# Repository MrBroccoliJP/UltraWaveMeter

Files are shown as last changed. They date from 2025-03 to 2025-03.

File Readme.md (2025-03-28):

 
# UltraWaveMeter 🌊📏

**UltraWaveMeter** is an Arduino-based ultrasonic measurement system designed to measure distances and detect waves using the **HC-SR04** ultrasonic sensor. It is built on the **ESP8266** microcontroller and supports real-time data logging, temperature-compensated calculations, and serial interface control.

<figure>
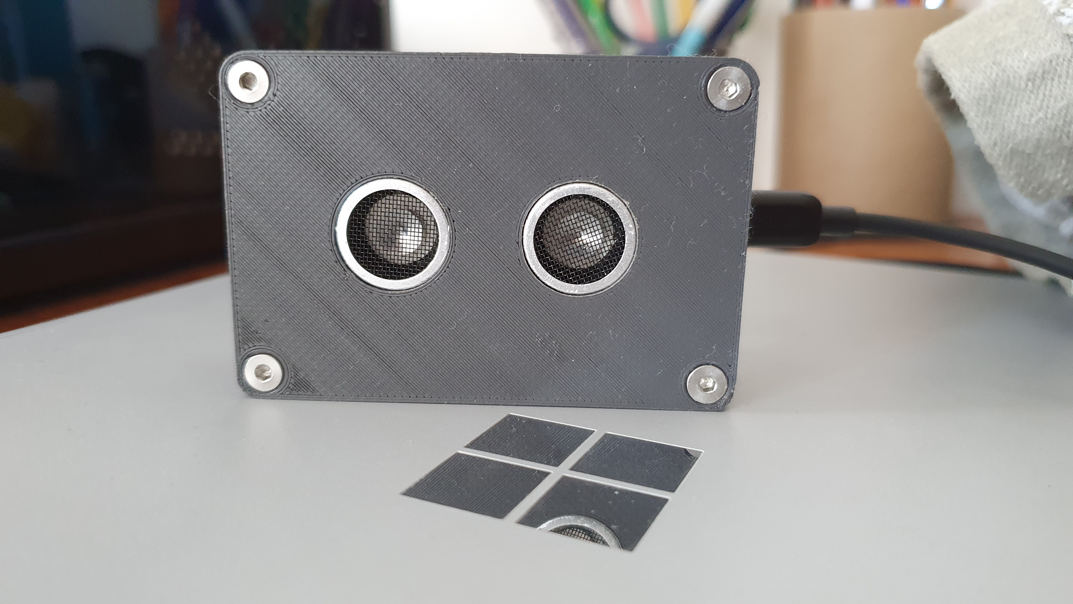
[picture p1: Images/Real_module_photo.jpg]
UltraWaveMeter - Final Assembled Module
    
    <figcaption>UltraWaveMeter - Final Assembled Module</figcaption>
</figure>

## About the Project  

This project was developed in collaboration with the [**Department of Civil Engineering at the University of Aveiro**](https://www.ua.pt/pt/decivil/). It was designed as a measurement device to analyze wave behavior in an artificial canal. The collected wave data was used to study the effects of different materials and techniques for **wave energy dissipation**, specifically in structures like breakwaters and seawalls—such as the **Paredão de Aveiro**.  

The module was custom-built to be attached to the **artificial canal** used for the experiment. Waves were artificially generated using a mechanical system, allowing researchers to test various **frequencies and amplitudes**.  

Upon completion, the module was delivered to a faculty professor along with an **instruction manual**, ensuring that it could be reused and easily adapted for future experiments.  

A prototype featured Wi-Fi connectivity for remote data transmission and control. However, due to time constraints and network configuration complexities, this feature was omitted from the final version.

<figure>
    UltraWaveMeter measuring wave behavior in an artificial canal
    <figcaption>UltraWaveMeter measuring waves in an artificial canal</figcaption>
</figure>

[Video example of the artificial waves](Images/Video.mp4)

## Features
* **Accurate Distance Measurement:** Uses an **HC-SR04** ultrasonic sensor.
* **ESP8266 Microcontroller:** For reliable data processing.
* **Temperature Compensation:** Ensures precise readings.
* **Real-time Serial Monitoring and Logging:** For immediate data analysis.
* **Adjustable Sampling Rate:** Provides flexibility in measurement frequency.
* **Physical Buttons & Remote Trigger:** Offers multiple control options.
* **Serial Commands:** Enables remote operation.
* **Durable Enclosure:** 3D printed using PETG for enhanced durability.

## Components
| Quantity | Component        | Model         |
|----------|-----------------|--------------|
| 1        | Microcontroller  | ESP8266      |
| 1        | Ultrasonic Sensor | HC-SR04     |
| 1        | Red LED         | Generic      |
| 1        | Resistor (330Ω) | Generic      |
| 3        | Push Button     | Generic      |
| 1        | USB Cable (Micro-USB)* | Generic |

###### *depends on the dev board used
## Wiring Diagram
The setup connects the **HC-SR04** sensor to the **ESP8266**, along with buttons for user input and an LED indicator. Ensure correct wiring to prevent malfunctions.   
BTN2 is a remote trigger button connected via a JST plug.

**Pin Assignments:**

| Component         | Pin  | GPIO |
|-------------------|------|------|
| BTN1              | D3   | GPIO 0|
| BTN2              | SD3  | GPIO 10|
| LED               | D0   | GPIO 16|
| RST Button        | RST  |    |
| HC-SR04 Trigger   | D6   | GPIO 13|
| HC-SR04 Echo      | D7   | GPIO 15|

<figure>
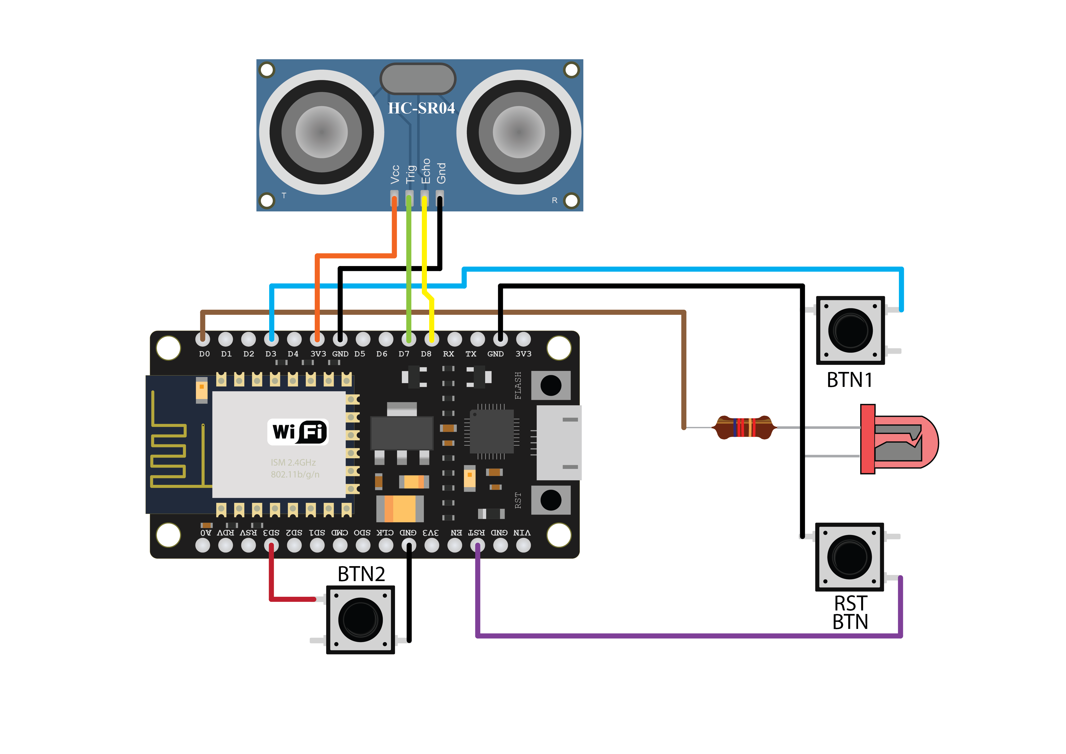
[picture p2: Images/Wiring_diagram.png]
UltraWaveMeter wiring diagram
    
    <figcaption>UltraWaveMeter wiring diagram </figcaption>
</figure>

<figure>
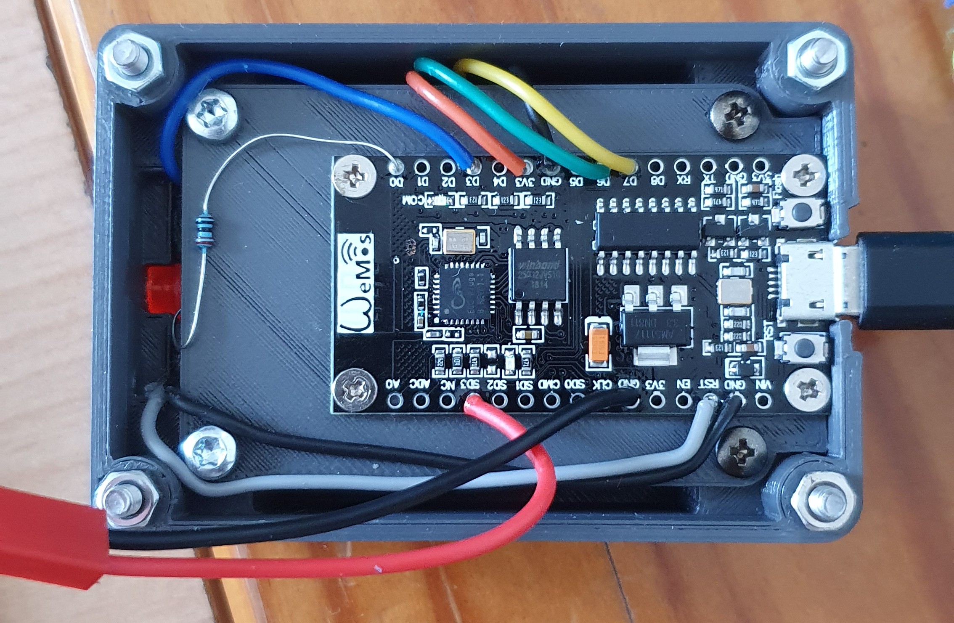
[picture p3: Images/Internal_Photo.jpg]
UltraWaveMeter internal photo
    
    <figcaption>UltraWaveMeter internal wiring and assembly </figcaption>
</figure>

## 3D Model and assembly 

The 3D model consists of three main parts. The shell is made up of two sections that screw together, forming a water-resistant enclosure for the electrical components. The ultrasonic sensor is securely held in place at the bottom, fitting snugly within the housing and pressed together with a tray that houses the ESP8266 dev board. The design prioritizes ease of assembly and maintenance, allowing for quick repairs in case of failure.

<figure>
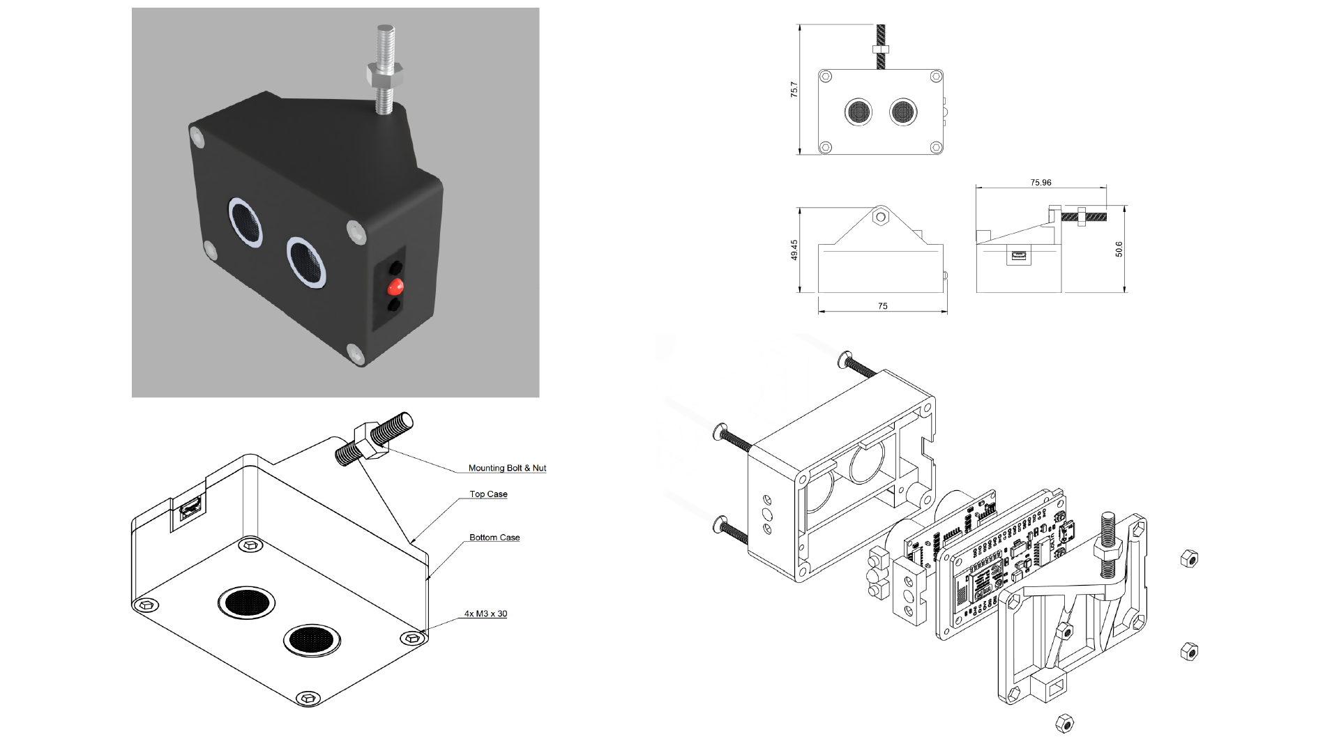
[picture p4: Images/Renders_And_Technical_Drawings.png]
3D Model, Renders, and Technical Drawings of the UltraWaveMeter Enclosure
    
    <figcaption>3D Model, Renders, and Technical Drawings of the UltraWaveMeter Enclosure </figcaption>
</figure>

The top and bottom enclosures are screwed together with an insulating material (silicone glue or a rubber gasket) to prevent water ingress, with additional silicone glue applied around the ultrasonic module tubes for further sealing.

### Remote Trigger Button (BTN2)

 - BTN2 uses a JST connector, glued and insulated to prevent water ingression, and a 3-meter cable for remote operation.  
  
<figure>
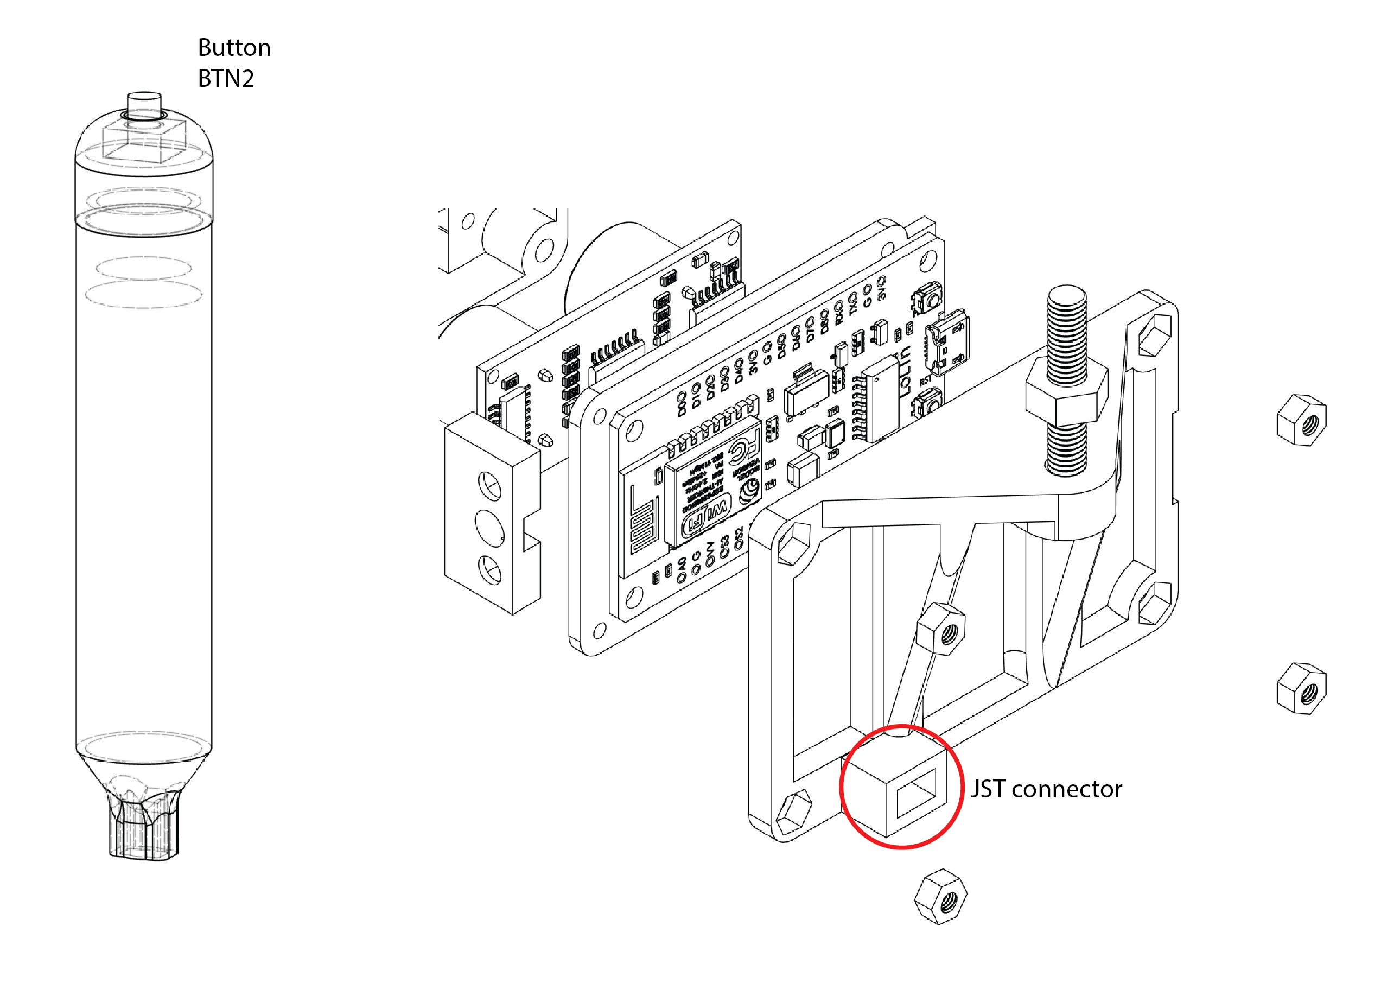
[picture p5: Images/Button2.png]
Waterproof Remote Trigger Button (BTN2) with JST Connector
    
    <figcaption>Waterproof Remote Trigger Button (BTN2) with JST Connector </figcaption>
</figure>

## Usage Instructions
1.  **Position:** Place the module above the measurement area.
2.  **Connect:** Connect the USB cable to a computer.
3.  **Open Serial Monitor:** Set the baud rate to 9600.
4.  **Temperature Input:** Enter the ambient temperature when prompted.
5.  **Start Measurement:**
    * Press Button 1, Button 2, or enter 'S' in the serial monitor.
    * Default sampling interval is 40ms.
    * To change, enter 'N' and specify a value >40ms.
6.  **Stop Measurement:**
    * Press Button 1, Button 2, or enter 'S'.
7.  **Save Data:**
    * Copy the serial monitor output for analysis.
8.  **Reset:**
    * Enter 'R' or press the reset button.

## Arduino Code / Sketch

### Deprecated Code
The version of the code in **Original_Portuguese** is now deprecated and is no longer actively maintained. Please use the version in **Translated_English** for the most up-to-date version of the software.

- **[Original Version (Portuguese)](Arduino_Sketch/Original_Portuguese/UltraWaveMeter/UltraWaveMeter.ino)** - Deprecated
- **[Updated Version (English)](Arduino_Sketch/Translated_English/UltraWaveMeter/UltraWaveMeter.ino)** - Recommended

## How the Sensor Works
The **HC-SR04** ultrasonic sensor emits a **40 kHz** sound wave that reflects off objects. The sensor calculates the time taken for the wave to return and determines the distance using the formula:

$$
\text{Distance (cm)} = \frac{\text{Speed of Sound (cm/μs)} \times \text{Echo Signal Duration (μs)}}{2}
$$  

With temperature compensation:  

$$
\text{Distance} = 0.034 \times \frac{\text{Echo}}{2} \times \frac{1 + T}{273.15} \times 60.368
$$  

## Example Output
<details>
  <summary>Example</summary>

```
PROGRAM STARTING

Enter ambient temperature: 23
23
Temperature saved
===== Program Initialized =====

Baseline distance: 124,5 cm 
Baseline distance: 125,1 cm 

Average: 124,8 cm 

Version: V5.0

Ultrasonic Wave Measurement System
To start measurements, press Button 1, Button 2, or enter 'S' in serial console.
To stop, press Button 1, Button 2, or enter 'S' in serial console.
To use a custom sample interval (default = 40ms), enter 'N'.
To RESET the system, enter 'R'.
****************************

Waiting to start -> Press Button 1 or Button 2 or enter 'S' OR 'N'
S

********** READING NUMBER: 1 **********
Baseline distance: 124,8 cm 
Baseline distance: 125,2 cm 
Baseline distance: 124,9 cm 
Baseline distance: 125,0 cm 
Baseline distance: 125,3 cm 

Baseline distance: Average = 125,04 cm 

Sample interval: 40ms 

DISTANCE (cm) || TIME (ms)

125,04 40
125,05 80
125,12 120
125,08 160
125,11 200
124,98 240
120,34 280
115,22 320
110,15 360
105,47 400
100,32 440
95,78 480
90,23 520
85,69 560
90,14 600
95,33 640
100,21 680
105,67 720
110,45 760
115,22 800
120,11 840
124,76 880
124,88 920
124,93 960
125,02 1000
S

Waiting to start -> Press Button 1 or Button 2 or enter 'S' OR 'N'
N

MODE 2

Enter desired sample interval in ms (minimum 40ms): 100
(...)
```

</details>

The data was then copied into Excel, where graphs were generated, and average, minimum, and maximum measurements were calculated. Relevant equations were applied to analyze the wave behavior and energy dissipation.

<figure>
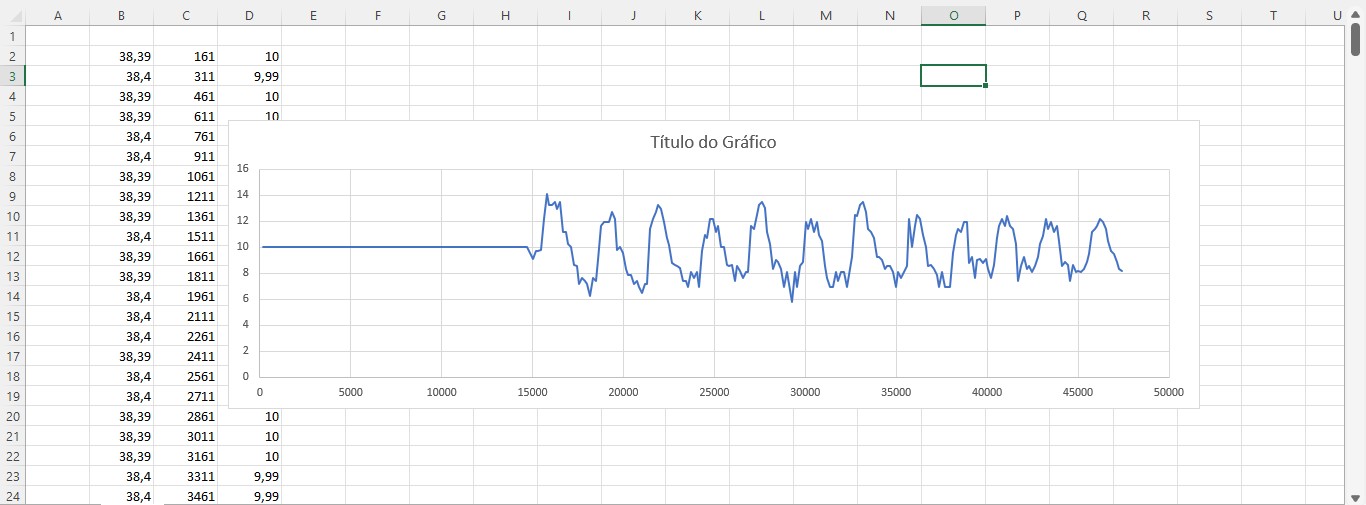
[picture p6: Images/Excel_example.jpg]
Analyzing UltraWaveMeter Data in Excel - Wave Behavior Graphs
    
    <figcaption>Analyzing UltraWaveMeter Data in Excel - Wave Behavior Graphs </figcaption>
</figure>

## Software
The system is programmed using **Arduino IDE** with the **NewPing** library by Tim Eckel. The library simplifies sensor interactions and improves accuracy.

### Useful Links
- [Arduino NewPing Library](https://www.arduino.cc/reference/en/libraries/newping/)
- [NewPing Documentation](https://bitbucket.org/teckel12/arduino-new-ping/wiki/Home)

------
## 📜 License
Developed by **João Fernandes**  

This project is licensed under the Creative Commons Attribution-NonCommercial 4.0 International License (CC BY-NC 4.0)

UltraWaveMeter © 2022-2025 by João Fernandes is licensed under Creative Commons Attribution-NonCommercial 4.0 International  

See the [LICENSE](LICENSE.txt) file for details  
Or visit:  
[http://creativecommons.org/licenses/by-nc/4.0/](http://creativecommons.org/licenses/by-nc/4.0/)  

or send a letter to:

Creative Commons
PO Box 1866  
Mountain View,    
CA 94042  
USA  

In summary (not a substitute for the full license):

 - You are free to share and adapt the material for non-commercial purposes
 - You must give appropriate credit and indicate if changes were made
 - You may not use the material for commercial purposes without specific permission

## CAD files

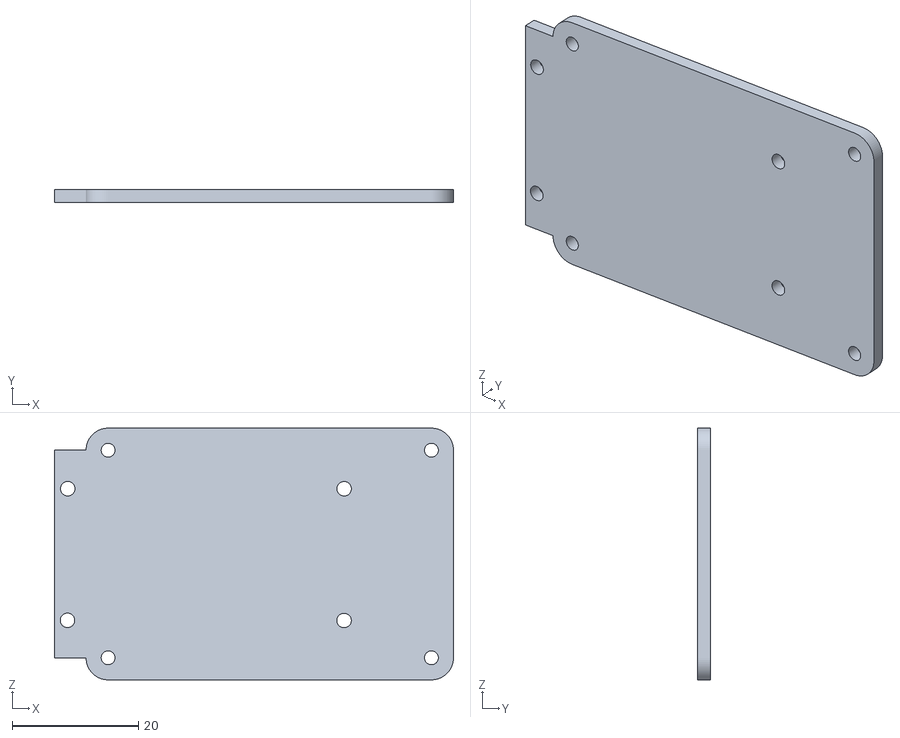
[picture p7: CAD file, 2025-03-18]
3D_Models/STL/Inner_esp_mounting_tray.stl
63.3 x 2.00 x 39.9

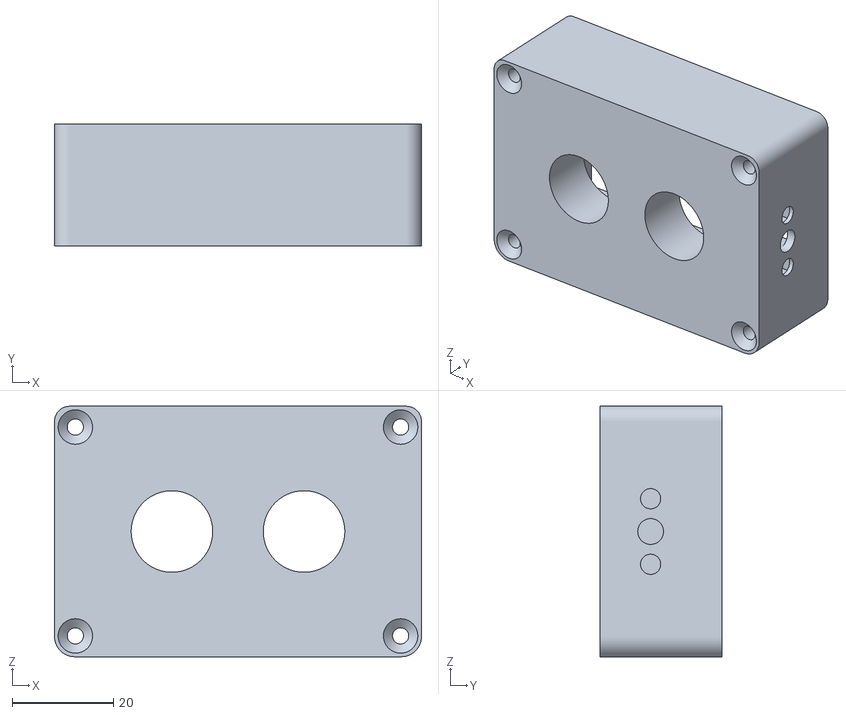
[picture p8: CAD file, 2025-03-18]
3D_Models/STL/Bot_case.stl
72.5 x 24.1 x 49.5

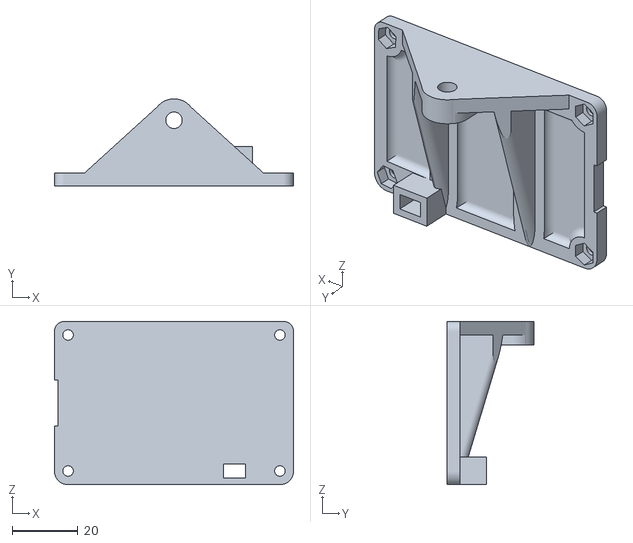
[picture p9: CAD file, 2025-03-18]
3D_Models/STL/Top_case.stl
72.5 x 26.5 x 49.5

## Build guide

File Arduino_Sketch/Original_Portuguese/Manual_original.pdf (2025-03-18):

# Sensor ultrassónico para medição de ondas

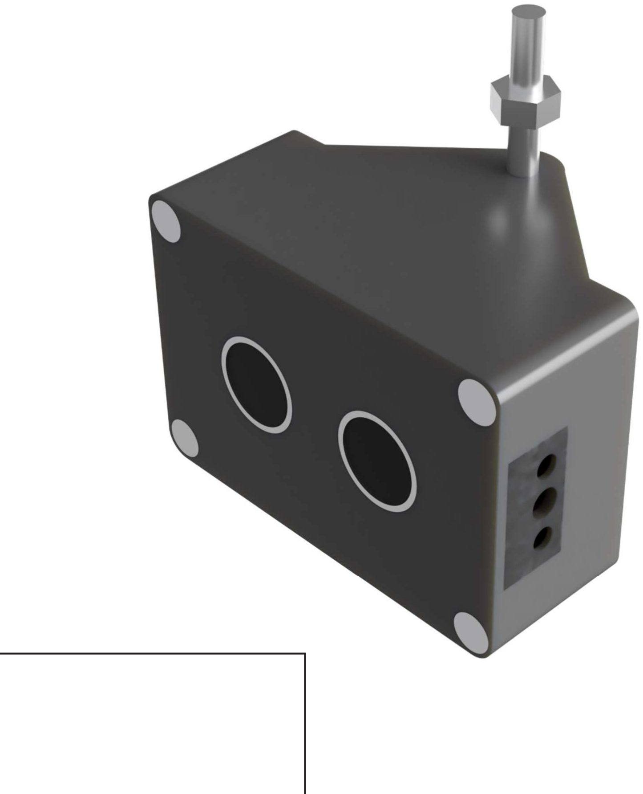
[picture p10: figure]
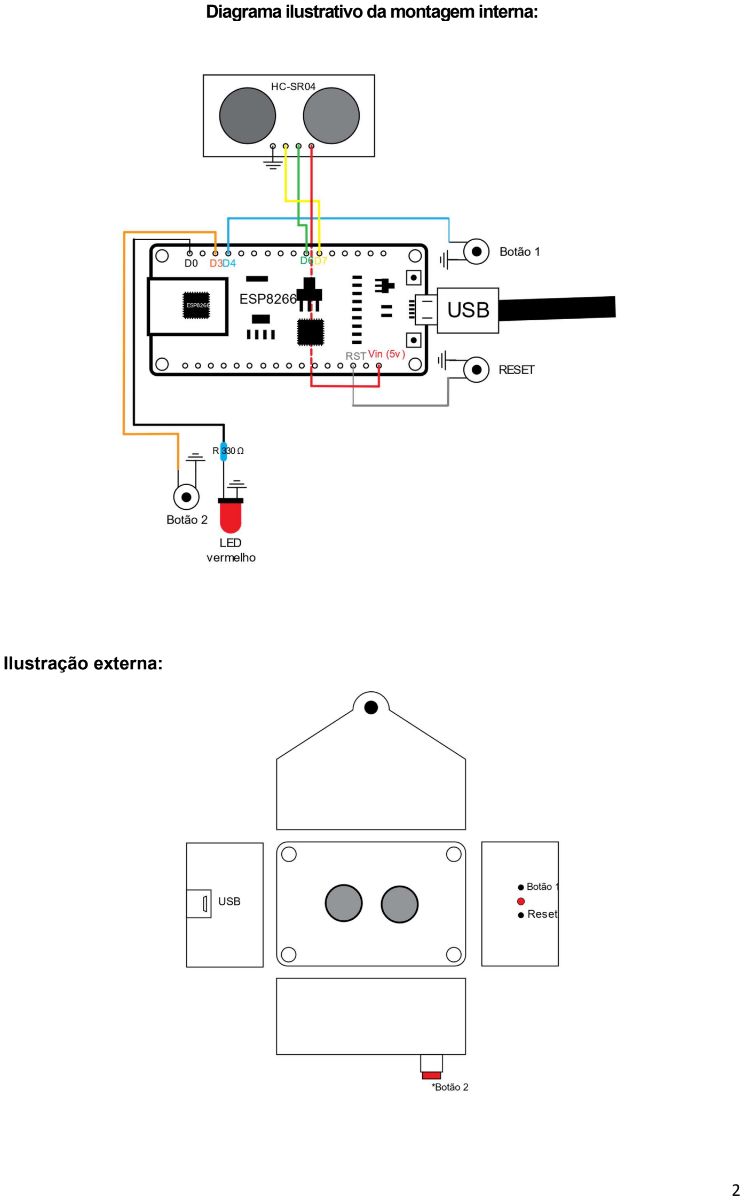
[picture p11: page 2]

Diagrama ilustrativo da montagem interna:

Ilustração externa:

Tabela de componentes:

QUANTIDADE | TIPO | MODELO
1 | Microcontrolador | ESP8266
1 | Sensor ultrassónico | HC-SR04
1 | LED vermelho | Genérico
1 | Resistência (330 Ω) | Genérico
3 | Botão momentâneo | Genérico

### 1 Cabo Micro-USB para USB

| 3m | Genérico

Instruções de uso:
1. Colocar o módulo numa posição acima do sítio onde se pretende efetuar a medida.
2. Ligar o cabo USB a um computador.

### 3. Abrir um programa com capacidade de monitor de série (por ex. Arduíno IDE):

a. Selecionar a taxa de transmissão recebida a: 9600

### 4. Seguir as instruções que serão mostradas no ecrã:

a. Inserir a temperatura ambiente e enviar

### 5. Começar uma contagem:

a. Usando o Botão 1, Botão 2 ou enviando “S” pelo monitor de série começa uma contagem com 40ms de intervalo entre cada medição.
b. Enviando “N” pelo monitor de série é possível começar uma nova medição com o intervalo entre amostras parametrizável:
i. Envie pelo monitor de série o intervalo que pretende (>40ms)

### 6. Parar uma contagem: Usando o Botão 1, Botão 2 ou enviando “S” pelo monitor de

série.

### 7. Copiar os dados do monitor de série e guardar num ficheiro a escolha, para

tratamento dos mesmos posteriormente.

Observação:

### 1. Se for necessário fazer reset ao microcontrolador pode-se enviar “R” pelo monitor de

série ou clicando no botão reset.

### 2. Para uso com Arduino ide: Arduino IDE -> Ferramentas -> Monitor

Observações finais:

O módulo é composto por um sensor ultrassónico “HC-SR04” que mede a distância de qualquer objeto até ao mesmo. Tem uma resolução de 0.3 Cm o que faz com que cada medida tenha uma incerteza de ±0.3Cm, tem alcance de 2cm até 400cm.

O sensor é composto por um transmissor e recetor, transmite uma onda com frequência de 40 kHz. Quando transmite a onda a onda é refletida e a mesma demora mais ou menos tempo dependendo da distância a que está o objeto. O sensor contém 4 conexões, sendo duas das mesmas de energia, e as duas de comunicação, um desses portos é denominada por “trigger” e outro é denominado de “echo”. Para ser efetuada uma medida o porto “trigger” tem de ser enviado um sinal alto durante 10µs, o módulo é então assim sinalizado que se pretende fazer uma medição. De seguida envia 8 sinais de 40kHz, através do envio de 8 sinais consegue minimizar o erro devido a interferências externas. Se nenhum dos sinais for obtido no transmissor o sensor envia um sinal alto através do porto “Echo” durante 38ms que sinaliza que a leitura não foi efetuada corretamente (Time-out). Se o sensor receber os sinais transmitidos coloca o porto “Echo” em sinal alto durante o tempo que o sinal demorou desde que foi transmitido até ser recebido. Usando esse tempo, podemos calcular a distância de um objeto relativamente ao sensor através da velocidade do som.

# ܦݐݏ ݋݋݋ ݏߤ

# ݏߤEcho݋݋ ݎݑܦ

# ܦݐݏ

Echo

Visto que a velocidade do som está relacionada com a densidade do material de propagação, e a densidade está por sua vez relacionada com a temperatura a que se encontra esse material, a equação teve de ser ajustada tendo em conta a temperatura ambiente.

# ܦݐݏ

Echo

כ

*Fórmula utilizada por recomendação dos criadores da livraria “NewPing”
Para operar o sensor foi usado um microcontrolador, neste caso baseado no microchip ESP8266. A tarefa deste microcontrolador coordenar os pedidos de leitura ao sensor e de seguida processar os dados que o sensor transmite para a distância em centímetros usando a fórmula acima.

O microcontrolador foi programado usando programação arduino. No código foi usada uma livraria “NewPing”, escrita por “Tim Eckel“, esta livraria foi escrita para agilizar o uso deste tipo de sensores sendo esta uma forma mais fácil e intuitiva de interagir com o sensor através do micro controlador. A livraria agilizou o desenvolvimento da interface e a mitigação de erros de medida pelo processamento de dados.

Links uteis:
https://www.arduino.cc/reference/en/libraries/newping/

Documentação:
https://bitbucket.org/teckel12/arduino-new-ping/wiki/Home

Em anexo está o código que foi escrito no microcontrolador à data.
Corresponde á Versão 5 do programa “Sensor ultrassónico para medição de ondas” programado em Arduíno.

João Fernandes

### 29 de Julho de 2022

1 //JOAO FERNANDES 2022
2 //SENSOR ULTRASONICO P
3
4
5 #include <NewPing.h>
6 #define TRIGGER_PIN 12 // Arduino pin tied to trigger pin on the ultrasonic sensor.
7 | #define ECHO_PIN 13 // Arduino pin tied to echo pin on the ultrasonic sensor.
8 #define MAX_DISTANCE 170 // Maximum distance we want to ping for (in centimeters). 9
10 NewPing sonar(TRIGGER_PIN, ECHO_PIN, MAX_DISTANCE); // NewPing setup of pins and maximum distance.
11
12 float temp = 25; // Temperature in Celsius (this value would probably come from a temperature sensor).
13 float factor = sqrt(1 + temp / 273.15)/ 60.368; // Speed of sound calculation based on temperature. //default value 25º
14 short int Mode = 0;
15 bool btnState;
16 unsigned long lastButtonPress = 0;
17 short int btnDelay = 250; //delay for debouncing 18 short int readingN = 0;
19 unsigned long ReadingStart = 0;
20 String READING;
21 String mydata;
22 float avg = 0;
23 String inst = "\nJoão Fernandes 2022\n Para começar leituras clique no botão 1, botão 2 ou insira 'S' no comando de série.\n Para parar clique no botão 1, botão 2 ou insira 'S' no comando de série.\n Para fazer uma leitura com um numero diferente de tempo entre amostras (default = 40ms) envie 'N'\n Para RESET envie 'R'";
24 String Code_version = "V5.0";
25 short int Rate = 40; //default
26
27 void setup() {
28 Serial.begin(9600);
29 pinMode(16, OUTPUT);
30 pinMode(0, INPUT_PULLUP); 31 pinMode(4, INPUT_PULLUP); 32
33 digitalWrite(16, HIGH); 34 delay(100);
35 digitalWrite(16, LOW);
36 delay(500);
37 digitalWrite(16, HIGH); 38 delay(100);
39 digitalWrite(16, LOW);
40 delay(1000);
41 Serial.print("\nPROGRAMA A INICIAR \n");
42 Serial.print("\nInsira a temperatura ambiente: "); 43
44 // while(!Serial.available()) {
45 while (!Serial || !Serial.available()) {
46
47 if (millis() % 250 == 0){
48 digitalWrite(16, HIGH);
49 }
50 else if (millis() % 100 == 0){ 51 digitalWrite(16, LOW);
52 }
53 if (millis() % 3000 == 0){
54 Serial.print("\nInsira a temperatura ambiente: "); 55 Serial.flush();
56 }
57 yield();
58 }
59
60
61 while (mydata.toInt() == 0){
62 mydata = Serial.readStringUntil('\n');
63 Serial.println(mydata);
64 Serial.println("Temperatura guardada\n===== Programa Iniciado =====\n"); 65 Serial.flush();
66 yield();
67 }

### 68 temp = mydata.toInt(); // Temperature in Celsius (this value would probably come

from a temperature sensor).

### 69 factor = sqrt(1 + temp / 273.15)/ 60.368; // Speed of sound calculation based on

temperature. //default value 25º 70
71 for (int i = 2; i > 0; i--) {
72 float readingB = ((float)sonar.ping_median(5)* factor); 73 avg = avg + readingB;
74 READING = "Distancia BASE: " +(String)readingB + " cm "; 75 READING.replace(".", ",");
76 Serial.println(READING);
77 delay(300);
78 }
79 avg = avg / 2;
80 READING = "\nMedia: " +(String)avg + " cm "; 81 READING.replace(".", ",");
82 Serial.println(READING);
83 Serial.print("\n Versão: ");
84 Serial.println(Code_version);
85 Serial.println(inst);
86 Serial.println("****************************\n");
87
88 Serial.println("A aguardar inicio -> Botão 1 ou Botão 2 ou escreva 'S' OU 'N' "); 89 Mode = 0;
90 }
91
92 void loop() {
93
94
95 if (Mode == 0){
96 mydata = "";
97 while (Mode == 0){
98
99
100 if (millis() % 500 == 0){ 101 digitalWrite(16, HIGH); 102 }
103 else if (millis() % 250 == 0){ 104 digitalWrite(16, LOW);
105 }
106
107 if (Serial.available() > 0){
108 mydata = Serial.readStringUntil('\n'); 109 Serial.println(mydata);
110
111 if (mydata == "S"){
112 Mode = 1;
113 Serial.flush();
114 }
115 else if (mydata == "R"){ 116 ESP.reset();
117 }
118 else if (mydata == "N"){ 119 Mode = 2;
120 Serial.flush();
121 }
122 else {
123 Serial.println("Modo inválido -> 'S' OU 'N'"); 124 mydata = "";
125 Serial.flush();
126 }
127 }
128
129 btnState = digitalRead(0); // read input value 130 if (btnState == LOW){
131 if (millis() - lastButtonPress > btnDelay){ 132 Mode = 1;
133 btnState == HIGH;
134 }
135 lastButtonPress = millis();
136 }
137 btnState = digitalRead(4); // read input value 138 if (btnState == LOW){

139 if (millis() - lastButtonPress > btnDelay){ 140 Mode = 1;
141 btnState == HIGH;
142 }
143 lastButtonPress = millis(); 144 }
145 yield();
146 }
147 }
148
149 else if (Mode == 2){
150 Rate = 0;
151 avg = 0;
152
153 Serial.print("\nMODO 2\n" );
154 Serial.print("\nInsira o numero de ms entre amostras pretendido (minimo 40ms): " );
155
156 while (Rate < 40){
157 if (Serial.available() > 0){
158 mydata = Serial.readStringUntil('\n');
159 if (mydata.toInt() > 40 && mydata.toInt() < 5000){ 160 Rate = mydata.toInt();
161 Serial.flush();
162 }
163 else if (mydata == "R"){ 164 ESP.reset();
165 }
166 else if (mydata == "S"){ 167 Mode = 0;
168 Serial.flush();
169 break;
170 }
171 else {
172 Serial.println("\nValor Inválido ('R' PARA RESET & 'S' Para voltar ao menu inicial)\nInsira um valor >40ms" ); 173 Serial.flush();
174 }
175 | // Serial.println(mydata);
176 | // Serial.println(mydata.toInt());
177 }
178 yield();
179 }
180
181 readingN++;
182 if(Mode != 0){
183 Serial.print("\n********** LEITURA NUMERO: " ); 184 Serial.print(readingN );
185 Serial.println(" **********" );
186
187 for (int i = 5; i > 0; i--) {
188 float readingB = ((float)sonar.ping_median(5)* factor); 189 avg = avg + readingB;
190 READING = "Distancia BASE: " +(String)readingB + " cm "; 191 READING.replace(".", ",");
192 Serial.println(READING);
193 delay(300);
194 }
195 avg = avg / 5;
196 READING = "\nDistancia BASE: Média = " +(String)avg + " cm "; 197 READING.replace(".", ",");
198 Serial.println(READING);
199 Serial.print("\nDISTÂNCIA (cm) || TEMPO (ms)\n\n");
200
201 ReadingStart = millis();
202 }
203
204 while (Mode != 0){
205
206 digitalWrite(16, HIGH);
207
208 if (Serial.available() > 0){
209 mydata = Serial.readStringUntil('\n');

210 if (mydata == "S"){
211 Mode = 0;
212 Serial.flush();
213 }
214 if (mydata == "R"){
215 ESP.reset();
216 }
217 }
218
219
220 btnState = digitalRead(0); // read input value 221 if (btnState == LOW){
222 if (millis() - lastButtonPress > btnDelay){ 223 Mode = 0;
224 btnState == HIGH;
225 }
226 lastButtonPress = millis();
227 }
228 btnState = digitalRead(4); // read input value 229 if (btnState == LOW){
230 if (millis() - lastButtonPress > btnDelay){ 231 Mode = 0;
232 btnState == HIGH;
233 }
234 lastButtonPress = millis(); 235 }
236
237 if (millis() % Rate == 0){
238
239 READING = String(((float)sonar.ping_median(1)* factor), 2)+ " " +(String)( millis() - ReadingStart)+ "\n" ; 240 READING.replace(".", ",");
241 Serial.print(READING);
242 Serial.flush();
243 }
244
245 yield();
246 }
247 }
248
249 else {
250 avg = 0;
251 readingN++;
252 Serial.print("\n********** LEITURA NUMERO: " ); 253 Serial.print(readingN );
254 Serial.println(" **********" );
255 | // Serial.print("BASE: ");
256 | // Serial.print(avg);
257 for (int i = 5; i > 0; i--) {
258 float readingB = ((float)sonar.ping_median(5)* factor); 259 avg = avg + readingB;
260 READING = "Distancia BASE: " +(String)readingB + " cm "; 261 READING.replace(".", ",");
262 Serial.println(READING);
263 delay(300);
264 }
265 avg = avg / 5;
266 READING = "\nDistancia BASE: Média = " +(String)avg + " cm ";
267 READING.replace(".", ",");
268 Serial.println(READING);
269 Serial.print("\n Intervalo de tempo entre amostras: 40ms \n\n DISTÂNCIA (cm) || TEMPO (ms)\n\n");
270
271 ReadingStart = millis();
272
273 while (Mode != 0){
274
275
276 digitalWrite(16, HIGH);
277
278 if (Serial.available() > 0){
279 mydata = Serial.readStringUntil('\n'); 280

281 if (mydata == "S"){
282 Mode = 0;
283 Serial.flush();
284 }
285 else if (mydata == "R"){ 286 ESP.reset();
287 }
288 else {
289 Serial.flush();
290 }
291 }
292
293
294 btnState = digitalRead(0); // read input value 295 if (btnState == LOW){
296 if (millis() - lastButtonPress > btnDelay){ 297 Mode = 0;
298 btnState == HIGH;
299 }
300 lastButtonPress = millis();
301 }
302 btnState = digitalRead(4); // read input value 303 if (btnState == LOW){
304 if (millis() - lastButtonPress > btnDelay){ 305 Mode = 0;
306 btnState == HIGH;
307 }
308 lastButtonPress = millis(); 309 }
310
311 if (millis() % 40 == 0){
312
313 READING = String(((float)sonar.ping_median(1)* factor), 2)+ " " +(String)( millis() - ReadingStart)+ "\n" ; 314 READING.replace(".", ",");
315 Serial.print(READING);
316 Serial.flush();
317 }
318
319 yield();
320 }
321 }
322
323 }
324
325 | //JOAO FERNANDES 2022 | -
326

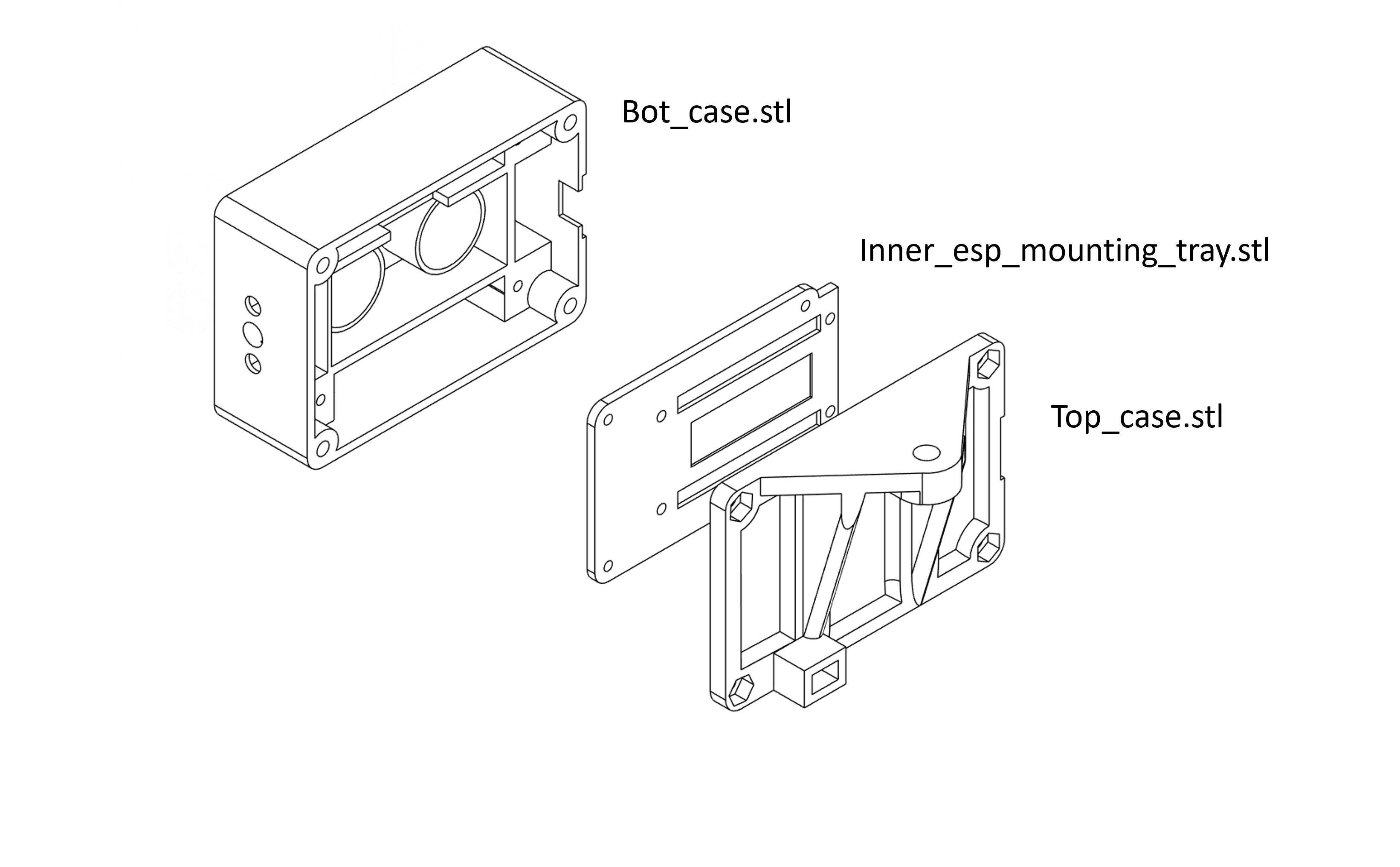
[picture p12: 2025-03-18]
3D_Models/3D_print_files_UltraWaveMeter.png

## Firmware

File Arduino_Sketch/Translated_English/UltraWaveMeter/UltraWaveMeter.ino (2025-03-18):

/**
 * UltraWaveMeter - Ultrasonic measurement system designed for precise distance and wave detection
 * Copyright (c) 2022-2025 João Fernandes
 * 
 * This work is licensed under the Creative Commons Attribution-NonCommercial 
 * 4.0 International License. To view a copy of this license, visit:
 * http://creativecommons.org/licenses/by-nc/4.0/
 * 
 * @author João Fernandes (Original author)
 * @version 6.0
 * @date 2022 (Original)
 * @date 2025 (Translation)
 * 
 * This program uses an ultrasonic sensor to measure distances over time,
 * which can be used for wave measurement applications. It provides different
 * measurement modes and outputs data via serial communication.
 */

#include <NewPing.h>

// Hardware configuration
#define TRIGGER_PIN 13     // Arduino pin connected to the ultrasonic sensor's trigger pin
#define ECHO_PIN 15        // Arduino pin connected to the ultrasonic sensor's echo pin
#define MAX_DISTANCE 170   // Maximum measurable distance in centimeters
#define LED_PIN 16         // Status LED pin
#define BUTTON_1_PIN 0     // First control button (INPUT_PULLUP) BTN1
#define BUTTON_2_PIN 10     // Second control button (INPUT_PULLUP) BTN2

// Initialize ultrasonic sensor with NewPing library
NewPing sonar(TRIGGER_PIN, ECHO_PIN, MAX_DISTANCE);

// Environment and calibration variables
float temp = 25;                        // Default ambient temperature in Celsius
float soundSpeedFactor;                 // Factor to calculate speed of sound based on temperature
float baselineAverage = 0;              // Average baseline measurement

// Program control variables
short int currentMode = 0;              // Operating mode (0: standby, 1: standard measurement, 2: custom interval)
bool buttonState;                       // Current state of buttons
unsigned long lastButtonPress = 0;      // Timestamp of last button press for debouncing
short int buttonDebounceDelay = 250;    // Delay for button debounce in milliseconds
short int readingCount = 0;             // Counter for measurement sessions
unsigned long measurementStartTime = 0; // Timestamp when measurement session started
short int sampleInterval = 40;          // Default time between samples in milliseconds (minimum 40ms)

// Serial communication variables
String measurementData;                 // Holds formatted measurement data for output
String serialInput;                     // Holds input from serial port

// User instructions and program information
String instructions = "\nUltrasonic Wave Measurement System\n"
                      "To start measurements, press Button 1, Button 2, or enter 'S' in serial console.\n"
                      "To stop, press Button 1, Button 2, or enter 'S' in serial console.\n"
                      "To use a custom sample interval (default = 40ms), enter 'N'.\n"
                      "To RESET the system, enter 'R'.";
String codeVersion = "V6.0";

/**
 * Initial setup function - runs once at program start
 */
void setup() {
  // Initialize serial communication
  Serial.begin(9600);
  
  // Configure pin modes
  pinMode(LED_PIN, OUTPUT);
  pinMode(BUTTON_1_PIN, INPUT_PULLUP);
  pinMode(BUTTON_2_PIN, INPUT_PULLUP);

  // LED startup sequence for visual confirmation
  digitalWrite(LED_PIN, HIGH);
  delay(100);
  digitalWrite(LED_PIN, LOW);
  delay(500);
  digitalWrite(LED_PIN, HIGH);
  delay(100);
  digitalWrite(LED_PIN, LOW);
  delay(1000);
  
  // Print startup message
  Serial.print("\nPROGRAM STARTING\n");
  Serial.print("\nEnter ambient temperature: ");

  // Wait for temperature input while blinking the LED
  while (!Serial || !Serial.available()) {
    // Blink LED while waiting
    if (millis() % 250 == 0) {
      digitalWrite(LED_PIN, HIGH);
    }
    else if (millis() % 100 == 0) {
      digitalWrite(LED_PIN, LOW);
    }
    
    // Periodically repeat the prompt
    if (millis() % 3000 == 0) {
      Serial.print("\nEnter ambient temperature: ");
      Serial.flush();
    }
    yield();  // Allow ESP8266 to handle system tasks
  }

  // Process temperature input
  serialInput = "";
  while (serialInput.toInt() == 0) {
    serialInput = Serial.readStringUntil('\n');
    Serial.println(serialInput);
    Serial.println("Temperature saved\n===== Program Initialized =====\n");
    Serial.flush();
    yield();
  }
  
  // Set temperature and calculate sound speed factor
  temp = serialInput.toInt();
  soundSpeedFactor = sqrt(1 + temp / 273.15) / 60.368;  // Speed of sound calculation based on temperature

  // Take initial baseline measurements
  for (int i = 2; i > 0; i--) {
    float baselineReading = ((float)sonar.ping_median(5) * soundSpeedFactor);
    baselineAverage += baselineReading;
    measurementData = "Baseline distance: " + (String)baselineReading + " cm ";
    measurementData.replace(".", ",");  // Format for CSV compatibility
    Serial.println(measurementData);
    delay(300);
  }
  
  // Calculate and display average baseline
  baselineAverage = baselineAverage / 2;
  measurementData = "\nAverage: " + (String)baselineAverage + " cm ";
  measurementData.replace(".", ",");
  Serial.println(measurementData);
  
  // Output program information and instructions
  Serial.print("\nVersion: ");
  Serial.println(codeVersion);
  Serial.println(instructions);
  Serial.println("****************************\n");
  Serial.println("Waiting to start -> Press Button 1 or Button 2 or enter 'S' OR 'N'");
  
  // Set initial mode to standby
  currentMode = 0;
}

/**
 * Main program loop
 */
void loop() {
  // MODE 0: Standby - waiting for user input to start measurement
  if (currentMode == 0) {
    serialInput = "";
    while (currentMode == 0) {
      // Status LED blink pattern for standby mode
      if (millis() % 500 == 0) {
        digitalWrite(LED_PIN, HIGH);
      }
      else if (millis() % 250 == 0) {
        digitalWrite(LED_PIN, LOW);
      }

      // Check for serial commands
      if (Serial.available() > 0) {
        serialInput = Serial.readStringUntil('\n');
        Serial.println(serialInput);

        // Process commands
        if (serialInput == "S") {
          currentMode = 1;  // Start standard measurement
          Serial.flush();
        }
        else if (serialInput == "R") {
          ESP.reset();      // Reset the system
        }
        else if (serialInput == "N") {
          currentMode = 2;  // Start custom interval measurement
          Serial.flush();
        }
        else {
          Serial.println("Invalid mode -> Use 'S' OR 'N'");
          serialInput = "";
          Serial.flush();
        }
      }

      // Check Button 1 state
      buttonState = digitalRead(BUTTON_1_PIN);
      if (buttonState == LOW) {
        if (millis() - lastButtonPress > buttonDebounceDelay) {
          currentMode = 1;  // Start standard measurement
          buttonState = HIGH;
        }
        lastButtonPress = millis();
      }
      
      // Check Button 2 state
      buttonState = digitalRead(BUTTON_2_PIN);
      if (buttonState == LOW) {
        if (millis() - lastButtonPress > buttonDebounceDelay) {
          currentMode = 1;  // Start standard measurement
          buttonState = HIGH;
        }
        lastButtonPress = millis();
      }
      
      yield();  // Allow ESP8266 to handle system tasks
    }
  }
  
  // MODE 2: Custom interval measurement
  else if (currentMode == 2) {
    sampleInterval = 0;
    baselineAverage = 0;

    Serial.print("\nMODE 2\n");
    Serial.print("\nEnter desired sample interval in ms (minimum 40ms): ");

    // Get valid interval input
    while (sampleInterval < 40) {
      if (Serial.available() > 0) {
        serialInput = Serial.readStringUntil('\n');
        
        // Process input
        if (serialInput.toInt() > 40 && serialInput.toInt() < 5000) {
          sampleInterval = serialInput.toInt();
          Serial.flush();
        }
        else if (serialInput == "R") {
          ESP.reset();
        }
        else if (serialInput == "S") {
          currentMode = 0;
          Serial.flush();
          break;
        }
        else {
          Serial.println("\nInvalid value ('R' for RESET & 'S' to return to main menu)\nEnter a value >40ms");
          Serial.flush();
        }
      }
      yield();
    }

    // Start new measurement session
    readingCount++;
    if (currentMode != 0) {
      Serial.print("\n********** READING NUMBER: ");
      Serial.print(readingCount);
      Serial.println(" **********");

      // Take baseline measurements
      for (int i = 5; i > 0; i--) {
        float baselineReading = ((float)sonar.ping_median(5) * soundSpeedFactor);
        baselineAverage += baselineReading;
        measurementData = "Baseline distance: " + (String)baselineReading + " cm ";
        measurementData.replace(".", ",");
        Serial.println(measurementData);
        delay(300);
      }
      
      // Calculate and display average baseline
      baselineAverage = baselineAverage / 5;
      measurementData = "\nBaseline distance: Average = " + (String)baselineAverage + " cm ";
      measurementData.replace(".", ",");
      Serial.println(measurementData);
      Serial.print("\nDISTANCE (cm) || TIME (ms)\n\n");

      // Record start time for relative time measurement
      measurementStartTime = millis();
    }

    // Continuous measurement loop
    while (currentMode != 0) {
      digitalWrite(LED_PIN, HIGH);  // LED on during measurement

      // Check for serial commands
      if (Serial.available() > 0) {
        serialInput = Serial.readStringUntil('\n');
        if (serialInput == "S") {
          currentMode = 0;
          Serial.flush();
        }
        if (serialInput == "R") {
          ESP.reset();
        }
      }

      // Check Button 1 state
      buttonState = digitalRead(BUTTON_1_PIN);
      if (buttonState == LOW) {
        if (millis() - lastButtonPress > buttonDebounceDelay) {
          currentMode = 0;
          buttonState = HIGH;
        }
        lastButtonPress = millis();
      }
      
      // Check Button 2 state
      buttonState = digitalRead(BUTTON_2_PIN);
      if (buttonState == LOW) {
        if (millis() - lastButtonPress > buttonDebounceDelay) {
          currentMode = 0;
          buttonState = HIGH;
        }
        lastButtonPress = millis();
      }

      // Take measurement at specified interval
      if (millis() % sampleInterval == 0) {
        measurementData = String(((float)sonar.ping_median(1) * soundSpeedFactor), 2) + " " + 
                          (String)(millis() - measurementStartTime) + "\n";
        measurementData.replace(".", ",");  // Format for CSV compatibility
        Serial.print(measurementData);
        Serial.flush();
      }

      yield();  // Allow ESP8266 to handle system tasks
    }
  }
  
  // MODE 1: Standard measurement with default 40ms interval
  else {
    baselineAverage = 0;
    readingCount++;
    
    Serial.print("\n********** READING NUMBER: ");
    Serial.print(readingCount);
    Serial.println(" **********");

    // Take baseline measurements
    for (int i = 5; i > 0; i--) {
      float baselineReading = ((float)sonar.ping_median(5) * soundSpeedFactor);
      baselineAverage += baselineReading;
      measurementData = "Baseline distance: " + (String)baselineReading + " cm ";
      measurementData.replace(".", ",");
      Serial.println(measurementData);
      delay(300);
    }
    
    // Calculate and display average baseline
    baselineAverage = baselineAverage / 5;
    measurementData = "\nBaseline distance: Average = " + (String)baselineAverage + " cm ";
    measurementData.replace(".", ",");
    Serial.println(measurementData);
    Serial.print("\nSample interval: 40ms \n\n DISTANCE (cm) || TIME (ms)\n\n");

    // Record start time for relative time measurement
    measurementStartTime = millis();

    // Continuous measurement loop
    while (currentMode != 0) {
      digitalWrite(LED_PIN, HIGH);  // LED on during measurement
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

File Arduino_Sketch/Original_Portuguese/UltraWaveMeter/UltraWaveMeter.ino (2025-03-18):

/**
 * UltraWaveMeter - Ultrasonic measurement system designed for precise distance and wave detection
 * Copyright (c) 2022-2025 João Fernandes
 * 
 * This work is licensed under the Creative Commons Attribution-NonCommercial 
 * 4.0 International License. To view a copy of this license, visit:
 * http://creativecommons.org/licenses/by-nc/4.0/
 * 
 * 
 * @author João Fernandes
 * @version 5.1
 * @date 2022
 * 
 * Este programa utiliza um sensor ultrassônico para medir distâncias ao longo do tempo,
 * que pode ser usado para aplicações de medição de ondas. Fornece diferentes
 * modos de medição e envia dados através de comunicação serial.
 */

#include <NewPing.h>

// Configuração do hardware
#define TRIGGER_PIN 13 // Pino do Arduino conectado ao pino de trigger do sensor ultrassônico
#define ECHO_PIN 15    // Pino do Arduino conectado ao pino de echo do sensor ultrassônico
#define MAX_DISTANCE 170 // Distância máxima de medição em centímetros

// Configuração da biblioteca NewPing para o sensor ultrassônico
NewPing sonar(TRIGGER_PIN, ECHO_PIN, MAX_DISTANCE);

// Variáveis de ambiente e calibração
float temp = 25;                                  // Temperatura em Celsius (valor padrão)
float factor = sqrt(1 + temp / 273.15) / 60.368;  // Cálculo do fator de velocidade do som baseado na temperatura
short int Mode = 0;                               // Modo de operação (0: espera, 1: medição padrão, 2: intervalo personalizado)
bool btnState;                                    // Estado atual dos botões
unsigned long lastButtonPress = 0;                // Timestamp do último estado do botão para debounce
short int btnDelay = 250;                         // Delay para debounce do botão em milissegundos
short int readingN = 0;                           // Contador para sessões de medição
unsigned long ReadingStart = 0;                   // Timestamp de quando a sessão de medição começou
String READING;                                   // Armazena dados formatados de medição para saída
String mydata;                                    // Armazena entrada da porta serial
float avg = 0;                                    // Média das medições base

// Instruções para o usuário e informações do programa
String inst = "\nJoão Fernandes 2022\n Para começar leituras clique no botão 1, botão 2 ou insira 'S' no comando de série.\n Para parar clique no botão 1, botão 2 ou insira 'S' no comando de série.\n Para fazer uma leitura com um numero diferente de tempo entre amostras (default = 40ms) envie 'N'\n Para RESET envie 'R'";
String Code_version = "V5.1";
short int Rate = 40; // Intervalo padrão entre amostras em milissegundos
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
